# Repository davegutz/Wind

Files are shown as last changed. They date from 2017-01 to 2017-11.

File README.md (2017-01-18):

# Wind
Lab Project
  Verify controllability of turbine system designed elsewhere.
  
# Installation Instructions
1.  Install Link Shell Extension  http://download.cnet.com/Link-Shell-Extension-64-bit/3000-2248_4-75213087.html
        It will make you restart explorer.    
    Link Shell Manual:  http://www.howtogeek.com/howto/16226/complete-guide-to-symbolic-links-symlinks-on-windows-or-linux/
2.  Install Arduino:  Get Arduino .zip
        i.  https://www.arduino.cc/en/Main/Software    get the Windows ZIP file for non-admin install
        ii. Unzip into your “My Documents”
            Ref:  https://www.arduino.cc/en/Guide/PortableIDE  Summary follows so shouldn’t have to go here
		iii.When installed, it creates folder Arduino-1.x.x where you told it to.   This is the "root" in what follows.
3.  Browse to Arduino-1.x.x, the root, in the unzipped Arduino..   Create a new directory called “portable” alongside the others
4.  Launch the Arduino executable “arduino.exe” found in the root.  This is the IDE.
    a.  Create/Save shortcuts to taskbar and Start
    b.  IDE-File - preferences - uncheck "Show verbose output during compilation" - set Compiler warnings = none.
        Be sure to click OK even if made no changes (do not press “X”).
    c.  Close the IDE.   The defaults are now set.
5.  Browse to <root>/portable/sketchbook (Arduino-1.x.x) to create symbolic link to source
	a.  Browse to this installation folder, where this README.md file is kept.   This is <source> in what follows.
    b.  right-click on myWindCode in  <source>\portable\sketchbook and “pick link source”
    c.  right-click in <root>\portable\sketchbook.  Right-click - Drop-as - Symbolic link.
6.  Open the IDE.   File-open-browse to potWind.ino.   Click it open.
    Close all other IDE windows so IDE remembers your default choice.
     Reference: https://www.arduino.cc/en/Reference/HomePage
        In brief:  Ctrl-r to compile.   Try it now with potWind.    Ask for help if this does not work.
                   Ctrl-u to compile/upload.   Arduino needs to be connected and USB free
7.  Install CoolTerm USB monitor
    http://freeware.the-meiers.org/CoolTerm_Win.zip
    Copy CoolTerm_0.stc in this folder to the desktop for easy starting of USB
8.  Habitually calibrate your ESC:
        - Open loop on board
        - Set POT to max
        - Power the ESC.   Wait for musical phrase followed by two beeps in quick succession
        - Set POT to min.   Wait for three beeps followed by one ready beep.
    Calibration may last 100 runs or it may last 1 run.   Motion of the POT
    can undo calibration if you're not hearing all the beeps.  
    Beware of this.   It's the most common problem.
    When you start up get in the habit of spot-checking calibration:
        - Nt moves at throttle 5-15 deg
        - 80% Nt at throttle 180 deg
9.  Normal startup
    - Microcontroller powered and at 0 deg throttle (either open or closed loop); wind power supply off
    - Turn on wind power supply.    Wait and should hear 3 beeps followed by 1
10. Control checkout
    It is possible to close the loop using embedded model before firing up the turbine and damaging something.
    In potWind.ino set bareOrTest=True, recompile, reload, and run without turbine powered.
    Observe output as though running with turbine (feedback switched internally).
    The CLAW embedded model will have an erroneous Ng(throttle) characteristic because the Arduino throughput will not support a table lookup here.

# FAQ
1.  Coolterm “Port not found.”  
    Rescan ports in Coolterm-Connection-Options
    Restart Coolterm if necessary
    Turn off Arduino IDE USB monitor
2.  Suddenly bad stability.   Recalibrate ESC.
    When you start up get in the habit of spot-checking calibration:
        - Nt moves at throttle 5-15 deg
        - 80% Nt at throttle 180 deg
3.  No response.  Check for loose wires on board.
4.  Poor response.   Check for reversed wires on ESC to 3-phase. 
    Confirm direction of airflow into inlet of gas generator.
5.  Arduino IDE:  port not found following ctrl-u
    Arduino-Tools-Port-Select Arduino
6.  Simulink Wind_SIM:  Invalid setting in 'Wind_SIM/ESC_Core_Tur/Rate_Transition1' for parameter 'InitCond'
    There is a NaN in data vector.  It is probably the first row.
    Open MOD.source file and delete offending row.   Resave it and rerun Wind_SIM.
7.  Arduino IDE:  When compiling, "The system cannot find the path specified."   This means the IDE is opened in the wrong folder.    Start another IDE session by Arduino - File - Open or Open Recent. 

8.  Simulink Wind_SIM:  Multiple messages running Simulink Wind_SIM:   "x-values must be increasing."  or "Unsupported input format." There is data corruption in DS.V, easily fixed by hand.  Open the csv file.  Plot "time" all by itself with no x-values using excel plot.    See dropout.   Browse to row indicated by x-param.
9.  Simulink Wind_SIM:  Transient truncated Simulink Wind_SIM running with vectors.   There are data dropouts in csv file.  Browse in csv file to the truncated time and delete bad rows of data.
10. Simulink Wind_SIM:  There is an apparent mismatch between Nts and Nt_ref.  You are probably running in "test" mode.    Look at Figure 2 for these.
11. Arduino IDE:  When compiling, "The systsem cannot find the path specified."  The  means the IDE is opened in the wrong folder.   Start another IDE session by using IDE Arduino - File - Open - or Open Recent.
12. Simulink Wind_SIM:   "Reference to non-existent field 'tFinal'."  Cannot open the csv file.  Probably named badly.
13. Simulink Wind_SIM:  "Error du to multiple causes."  "Reference to non-existent field 'vpot'".  You have "CALIBRATING" set in myWindCode.ino.   You can re-run or rename vf2v to vpot in csv file and ignore it but this will cause initialization to go badly.   So write the real vpot into csv file as constant.
14.  Simulink Wind_SIM:  Why does Nts not equal NtsD?   Ng in the Simulink model is assumed to follow nominal trend, so same software logic can be used all units.   The real Ng is not nominal and will differ.

# Expected Results
Set "#define VECTOR" in potWind.ino
Recompile and upload
Select open or close loop mode as desired on board
Start CoolTerm data save
Press pushbutton on board to begin defined vector test
Stop CoolTerm data save when done
Compare to Saves/v<your kit #>_2017

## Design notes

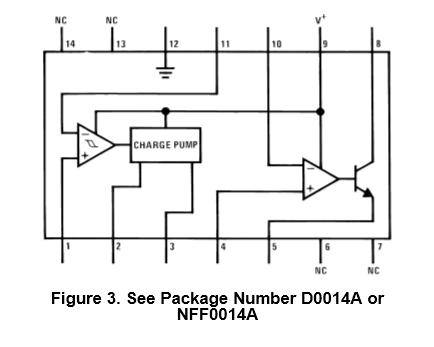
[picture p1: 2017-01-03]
Documentation/LM2907/LM2907 Schematic.PNG

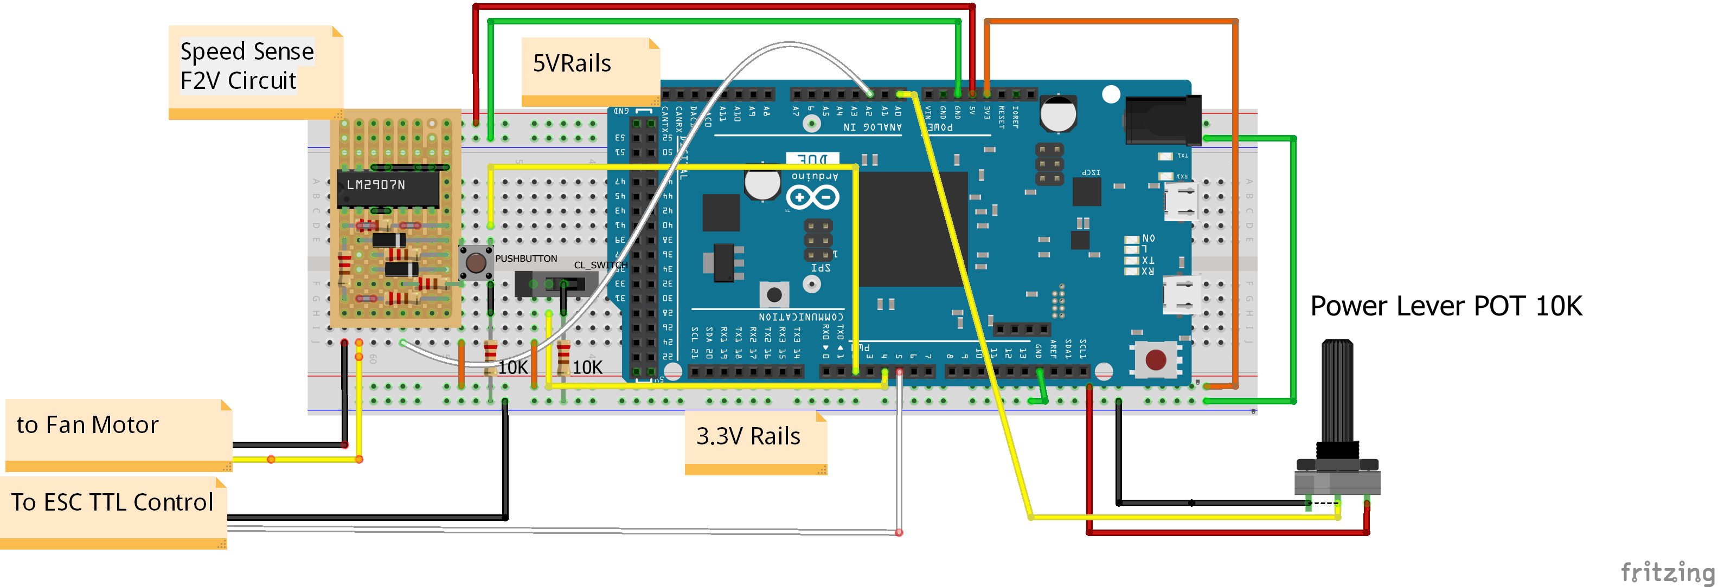
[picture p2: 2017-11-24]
Documentation/arduinoDUE_Wind_bb.png

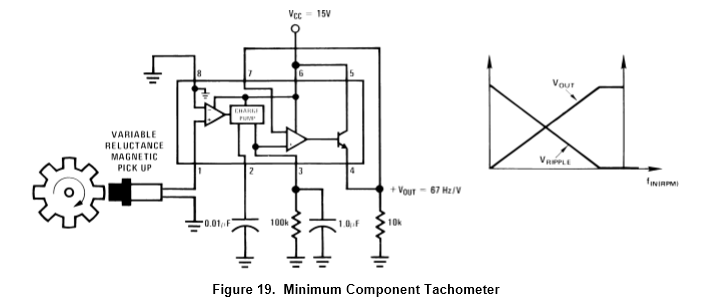
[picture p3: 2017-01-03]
Documentation/LM2907/LM2907 Circuit.PNG

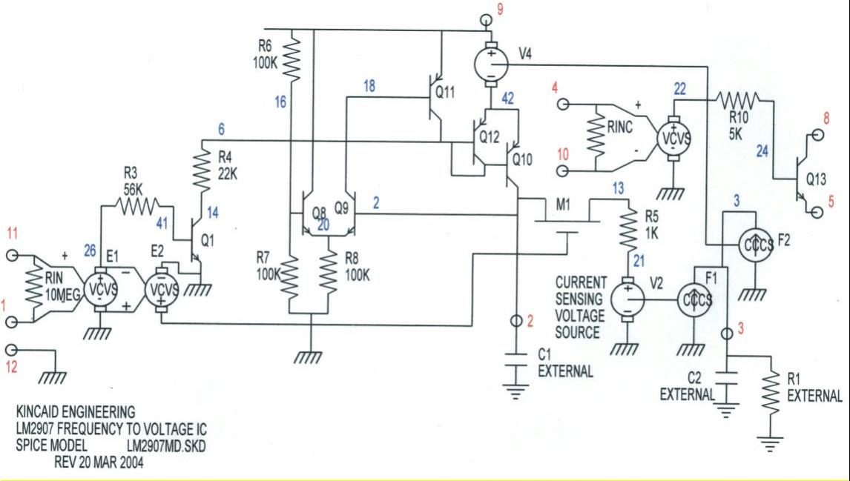
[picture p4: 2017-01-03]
Documentation/LM2907/LM2907.jpg

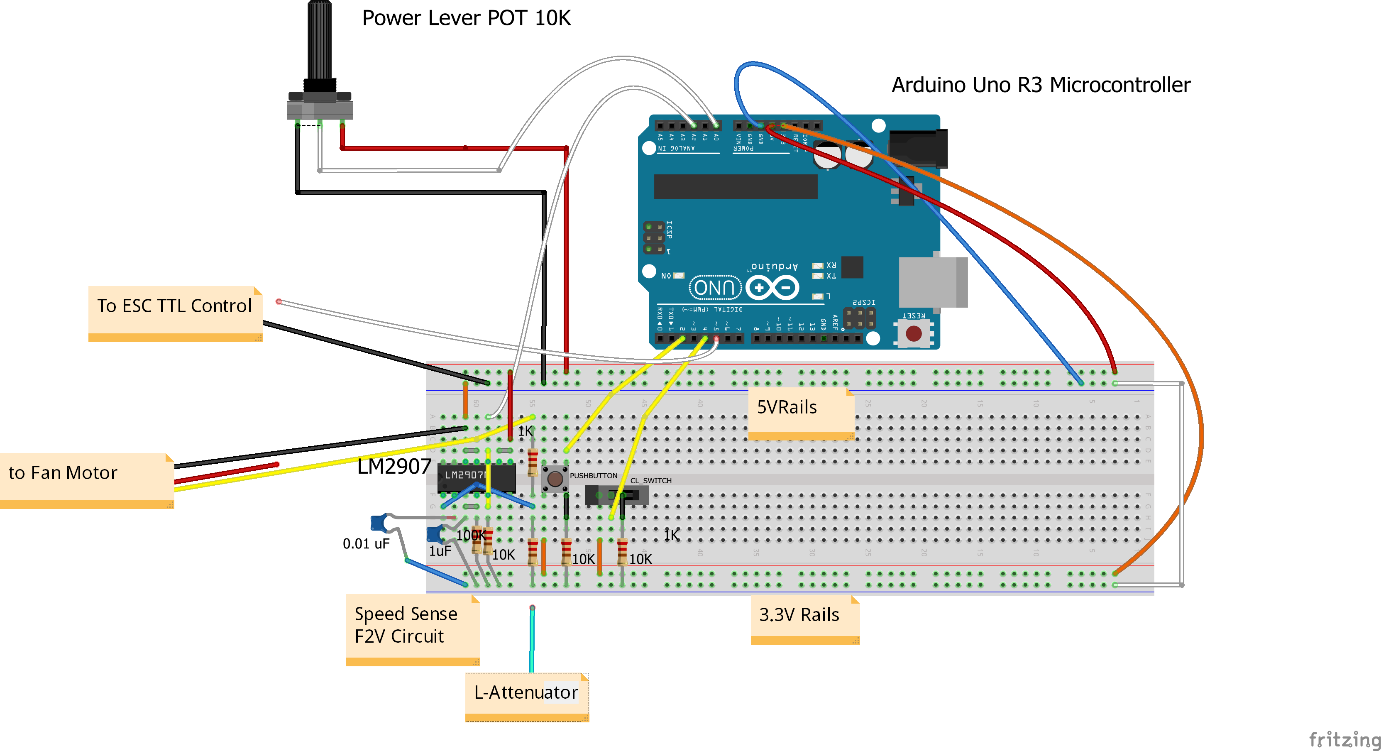
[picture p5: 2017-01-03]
Documentation/arduinoWind.png

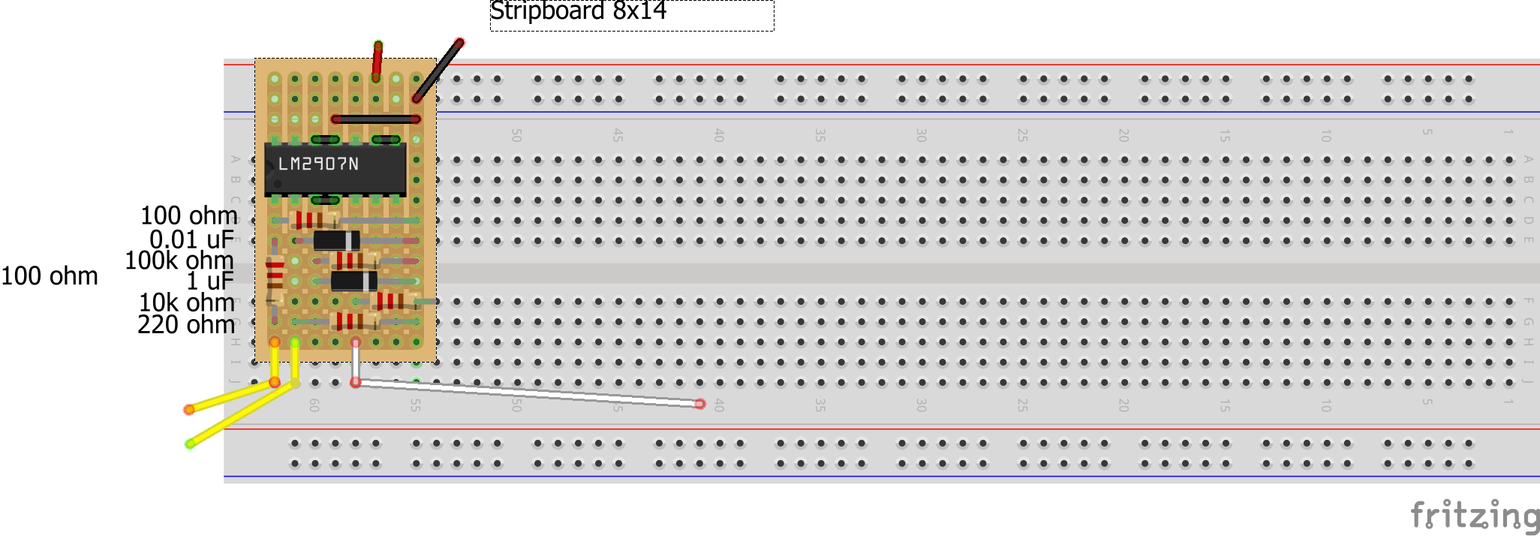
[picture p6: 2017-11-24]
Documentation/speedSenseStripboard_bb.png

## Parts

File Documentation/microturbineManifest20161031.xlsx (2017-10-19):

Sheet: 20161031
Manufacturer | Description | Part No | Source | Price Ea | Qty | Total | Shipping/Tax | $199.52
Hobby King | 50mm Alloy EDF 4800 kv (3s version) | Item# 20014254188 - 2x #107000044/22947 | https://hobbyking.com/en_us/hobbykingtm-50mm-alloy-edf-4800kv-3s-version.html | $20.26 | 2 | $40.52 | $8.43 | $48.95
Turnigy | Plush 25amp Speed Controller ESC | B00URCM4QO | http://www.hobbyking.com/hobbyking/store/__68532__TURNIGY_Plush_25amp_Speed_Controller_w_BEC_AR_Warehouse_.html | $18.89 | 1 | $18.89 | $6.96 | $25.85
Arduino | Uno R3 | A000066 | https://www.amazon.com/gp/product/B006H06TVG/ref=oh_aui_detailpage_o01_s00?ie=UTF8&psc=1 | $18.59 | 1 | $18.59 | $0.00 | $18.59
BINZET | Charger AC 100-240V to DC 12V 10A |  | https://www.amazon.com/gp/product/B00PK0N14M/ref=oh_aui_detailpage_o05_s00?ie=UTF8&th=1 | $17.99 | 1 | $17.99 | $0.00 | $17.99
Elegoo | Fun Kit | LYSB01ERPEMAC-ELECTRNCS | https://www.amazon.com/gp/product/B01ERPEMAC/ref=oh_aui_detailpage_o00_s00?ie=UTF8&psc=1 | $16.86 | 1 | $16.86 | $0.00 | $16.86
Fernco | PVC Couplings 2". Drill 7/32" hole for wires | P1056-22 | http://www.homedepot.com/p/2-in-x-2-in-DWV-Flexible-PVC-Coupling-P1056-22/100096490;jsessionid=FD5ADC11436A2B9FE7E68686A5A1567B | $4.99 | 2 | $9.98 | $0.56 | $10.54
Veranda | Cellular PVC Trim, 3/4 x 2-1/2 x 8' cut to 5" | H190JWS5 | http://www.homedepot.com/p/Veranda-3-4-in-x-2-1-2-in-x-8-ft-Cellular-PVC-Trim-H190JWS5/100243235 | $9.97 | 1 | $9.97 | $0.56 | $10.53
Home Depot | Toolbox | 17331512 | http://www.homedepot.com/p/The-Home-Depot-19-in-Plastic-Tool-Box-with-Metal-Latches-and-Removable-Tool-Tray-17331512/202021300 | $8.97 | 1 | $8.97 | $0.50 | $9.47
Mouser | Mouser Shipping | --- | http://www.mouser.com | $0.00 | 1 | $0.00 | $8.00 | $8.00
BW | 20 pairs 2mm Gold Plated Bueelt Banana Plug Connectors for ESC Batter |  | https://www.amazon.com/gp/product/B00T5SW7FE/ref=oh_aui_detailpage_o08_s00?ie=UTF8&psc=1 | $6.89 | 1 | $6.89 | $0.00 | $6.89
Generic | PVC Pipe 2" Sch 40, cut to 5" | 531137 | http://www.homedepot.com/p/2-in-x-10-ft-280-PSI-Schedule-40-PVC-DWV-Plain-End-Pipe/100161954 | $6.38 | 1 | $6.38 | $0.36 | $6.74
Commercial Electric | 3-way extension plug for 115 AC | # LA-05 | http://www.homedepot.com/p/Commercial-Electric-15-Amp-Triplex-Outlet-Swivel-Tap-White-LA-05/204836952 | $4.58 | 1 | $4.58 | $0.26 | $4.84
Generic | Pencil box > 6-3/4x4-1/2x1-1/2 inside |  | https://www.amazon.com/ADVANTUS-Polypropylene-Pencil-Inches-34104/dp/B0014DZE8K?s=office-products | $3.95 | 1 | $3.95 | $0.22 | $4.17
Gardner Bender | Shrink Tubing, 5 pk 3/16" black | HST-187B | http://www.homedepot.com/p/Gardner-Bender-3-16-in-Black-Polyolefin-Heat-Shrink-Tubing-5-Pack-HST-187B/202797315 | $1.99 | 1 | $1.99 | $0.11 | $2.10
Texas Instruments | Demodulator 10 kHz, through hole | LM2907N/NOPB | http://www.mouser.com/Search/ProductDetail.aspx | $1.91 | 1 | $1.91 | $0.00 | $1.91
Alpha | Potentiometer Linear, 10K, 20%, 500V | RV24AF-22-15R1-B10K-3LA | http://www.mouser.com/Search/ProductDetail.aspx | $1.61 | 1 | $1.61 | $0.00 | $1.61
Kemet | Cap .01 uF 5% 50 VDC | SMR5103J50J01L16.5CBULK | http://www.mouser.com/Search/ProductDetail.aspx | $0.63 | 1 | $0.63 | $0.04 | $0.67
Vimex | Slide Switch SPDT, 30V 200mA | 612-EG1218 | http://www.mouser.com/ProductDetail/E-Switch/EG1218/?qs=sGAEpiMZZMtHXLepoqNyVZDOWY7elTCOE4MJ3sXRkSs%3d | $0.56 | 1 | $0.56 | $2.13 | $2.69
Kemet | Cap 1 uF, 20 VDC, 5% | T356A105J020AT | http://www.mouser.com/ProductDetail/Kemet/T356A105J020AT/?qs=sGAEpiMZZMtZ1n0r9vR22XCieDCNbX8FzsYaQmMDgkk%3d | $0.85 | 1 | $0.85 | $0.05 | $0.90
Kemet | Cap 10 uF, 25 VDC, 20% | EEA-GA1E100 | http://www.mouser.com/ProductDetail/Panasonic/EEA-GA1E100/ | $0.22 | 1 | $0.22 | $0.01 | $0.23
Lenovo | Thinkpad X1 Laptop, GE Provided | n/a | n/a | - | 1 | - | - | -
Arduino | Portable IDE | n/a | https://www.arduino.cc/en/Guide/PortableIDE | - | 1 | - | - | -

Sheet: 20171019
Manufacturer | Description | Part No | Source | Price Ea | Qty | Total | Shipping/Tax | $347.36
BINZET | Spare power supplies | Charger AC 100-240V to DC 12V 10A | https://www.amazon.com/gp/product/B00PK0N14M/ref=oh_aui_search_detailpage?ie=UTF8&psc=1 | $17.99 | 2 | $35.98 | $0.00 | $35.98
Arduino | PLC for Simulink | DUE | https://www.amazon.com/Arduino-org-A000062-Arduino-Due/dp/B00A6C3JN2?s=electronics | $44.47 | 5 | $222.35 | $0.00 | $222.35
Toshiba | MOSFET for auto calibrate | TK40A06N1 | http://www.mouser.com/Search/ProductDetail.aspx | $0.98 | 6 | $5.88 | $0.00 | $5.88
Meder | Relays for auto calibrate | SIL03-1A72-71D | http://www.mouser.com/ProductDetail/MEDER-electronic-Standex/SIL03-1A72-71D/ | $3.98 | 6 | $23.88 | $0.00 | $23.88
Bourns | Carbon Potentiometers for Noise | PTD901-1015K-B103 | http://www.mouser.com/ProductDetail/Bourns/PTD901-1015K-B103/?qs=sGAEpiMZZMtC25l1F4XBU4LIzrlRxKBZVvfXJLawdTQ%3d | $1.68 | 5 | $8.40 | $0.00 | $8.40
Home Depot | PVC for base mounts, 3/4 x 7-1/4 x 96 | H190RWS4 | http://www.homedepot.com/p/Veranda-HP-3-4-in-x-7-1-4-in-x-8-ft-High-Performance-Cellular-PVC-Trim-H190RWS4/100290245 | $27.97 | 1 | $27.97 | $0.00 | $27.97
Hobby King | Spare turbine blades |  | https://hobbyking.com/en_us/rotor-for-hobbyking-alloy-50mm-edf-unit.html | $1.98 | 5 | $9.90 | $5.00 | $14.90
Mouser | Mouser Shipping | --- | http://www.mouser.com | $0.00 | 1 | $0.00 | $8.00 | $8.00
 |  |  |  |  |  | $0.00 | $0.00 | $0.00

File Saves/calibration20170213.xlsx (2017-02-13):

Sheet: Ard0_Turn0_ESC0_G0b_T0a
Description | Set Nt | TTL, ms | throttleFlt, deg | v4, vdc | Charger V, vdc | Charger I, A | Tng, micros | Ttur, micros |  | Charger Pwr, W | Throttle, deg | ln(Throttle) | FreqNg, Hz | FreqTur, Hz | Ng, RPM | Nt, RPM | Ng, % | Nt, % | Throttle, deg | Charger Pwr, W | Ng Pwr, W | Ng Pwr, SHP | Ng Total Torque, ft-lbf | Ng Torque, ft-lbf | Thrust, N | Thrust Power, W | Overall Efficiency | Vw, m/s | Vw, mph | Vt, m/s | Lambda tip speed ratio | dCpdLambda | simulate vpot from throttle | model throttle from vpot | Model Ng from Model Throttle, rpm | Model Ng from Model Throttle, % | Model pcntRef from Model Ng, % | Model Ng from pcntRef at RESET, % | Model Nt from Model Ng, % | Model Nt from Model Ng, rpm | Model Qg from Model Ng, ft-lbf | Model PwrG from Model Ng*Q, shp | Model dQgdNg, ft-lbf/rpm | Model TauG | Model dQtdNt, ft-lbf/rpm | Model TauT from wind | v4, vdc
DC Power Overhead | n/a | 1.03 | 6.07 | 0.0032 | 12.24 | 0.019 | 1e+32 | 1e+32 |  | 0.2 | 6.07 | 1.8027 | 1e-26 | 1e-26 | 6e-25 | 0 | 1.302083333e-27 | 0 | 6.066122035 | 0.23 | 0 | 0.0000 | 0.00000 | 0.00000 | 9.768434808e-87 | 9.469612349e-129 |  | 1.938818764e-42 | 4.362342218e-42 | 0 | 0.00 |  | 0.169 | 6.066 | 0.00 | 0.00 | -17.48 | 0.03 |  | 0 |  |  |  |  |  |  | 0.0032
Lowest Ng | n/a | 1.05 | 9 | 0.0024 | 12.15 | 0.34 | 7080 | 1e+32 |  | 4.1 | 9 | 2.1972 | 141.2429379 | 1e-26 | 8474.576271 | 6e-25 | 18.39100753 | 1.302083333e-27 | 9 | 4.07 | 3.83769 | 0.0051 | 0.00319 | 0.00000 | 0.028 | 0.04 | 1.1 | 3.25 | 7.3 | 1.727875959e-27 | 5.309152921e-28 |  | 0.250 | 9.000 | 4918.12 | 10.67 | -7.36 | 10.70 |  | 0 | 0.00000 | 0.00000 | 1.105647023e-07 |  |  |  | 0.0024
First Nt | tbd | 1.11 | 20 | 0.069 | 12.14 | 0.86 | 4040 | 68000 |  | 10.5 | 20 | 2.9957 | 247.5247525 | 14.70588235 | 14851.48515 | 882.3529412 | 32.22978548 | 1.914828431 | 20 | 10.45 | 10.22 | 0.0137 | 0.00485 | 0.00166 | 0.148 | 0.56 | 5.4 | 7.55 | 17.0 | 2.5 | 0.34 |  | 0.556 | 20.000 | 14872.75 | 32.28 | 13.10 | 32.29 | 13.1 | 6038.54 | 0.00194 | 0.00548 | 3.729326807e-07 | 0.100 |  |  | 0.069
Dynamic Nt #1 | 16 | 1.14 | 25 | 0.51 | 12.14 | 1.13 | 3680 | 8500 |  | 13.7 | 25 | 3.2189 | 271.7391304 | 117.6470588 | 16304.34783 | 7058.823529 | 35.38269928 | 15.31862745 | 25 | 13.72 | 13.49 | 0.0181 | 0.00583 | 0.00264 | 0.196 | 0.85 | 6.2 | 8.68 | 19.5 | 20.3 | 2.34 |  | 0.694 | 25.000 | 17654.58 | 38.31 | 18.82 | 38.33 | 18.8 | 8674.185965 | 0.00308 | 0.01034 | 4.462516013e-07 | 0.084 | -1.105608516e-07 | 0.339 | 0.51
Dynamic Nt #2 | 20 | 1.19 | 35 | 0.801 | 12.11 | 1.838 | 2980 | 5420 |  | 22.3 | 35 | 3.5553 | 335.5704698 | 184.501845 | 20134.22819 | 11070.1107 | 43.69407159 | 24.02367774 | 35 | 22.26 | 22.03 | 0.0295 | 0.00770 | 0.00452 | 0.369 | 2.20 | 9.9 | 11.92 | 26.8 | 31.9 | 2.67 |  | 0.972 | 35.000 | 21849.23 | 47.42 | 27.45 | 47.43 | 27.4 | 12648.40654 | 0.00518 | 0.02155 | 5.568072553e-07 | 0.067 | -1.517220518e-07 | 0.247 | 0.801
Dynamic Nt #3 | 25 | 1.30 | 54 | 1.167 | 12.06 | 3.18 | 2390 | 3740 |  | 38.4 | 54 | 3.9890 | 418.4100418 | 267.3796791 | 25104.60251 | 16042.78075 | 54.4804742 | 34.81506239 | 54 | 38.35 | 38.12 | 0.0511 | 0.01069 | 0.00750 | 0.716 | 5.94 | 15.5 | 16.59 | 37.3 | 46.2 | 2.78 |  | 1.500 | 54.000 | 27255.18 | 59.15 | 38.56 | 59.15 | 38.6 | 17770.27059 | 0.00857 | 0.04450 | 6.992882824e-07 | 0.054 | -2.112400453e-07 | 0.177 | 1.167
Dynamic Nt #4 | 36 | 1.36 | 64 | 1.275 | 12.03 | 3.96 | 2170 | 3260 |  | 47.6 | 64 | 4.1589 | 460.8294931 | 306.7484663 | 27649.76959 | 18404.90798 | 60.00384025 | 39.94120654 | 64 | 47.64 | 47.41 | 0.0636 | 0.01208 | 0.00889 | 0.956 | 9.17 | 19.2 | 19.18 | 43.2 | 53.0 | 2.76 |  | 1.778 | 64.000 | 29373.23 | 63.74 | 42.92 | 63.75 | 42.9 | 19777.02234 | 0.01011 | 0.05657 | 7.551124993e-07 | 0.050 | -2.441650521e-07 | 0.153 | 1.275
Dynamic Nt #5 | 45 | 1.50 | 90 | 1.597 | 11.95 | 5.94 | 1860 | 2690 |  | 71.0 | 90 | 4.4998 | 537.6344086 | 371.7472119 | 32258.06452 | 22304.83271 | 70.00448029 | 48.40458488 | 90 | 70.98 | 70.75 | 0.0949 | 0.01545 | 0.01226 | 1.518 | 18.35 | 25.8 | 24.17 | 54.4 | 64.2 | 2.658 |  | 2.500 | 90.000 | 33623.41 | 72.97 | 51.66 | 72.97 | 51.7 | 23803.85519 | 0.01356 | 0.08682 | 8.67131732e-07 | 0.043 | -3.076831315e-07 | 0.122 | 1.597
Dynamic Nt #6 | 50 | 1.69 | 125 | 1.95 | 11.84 | 8.59 | 1620 | 2210 |  | 101.7 | 125 | 4.8283 | 617.2839506 | 452.4886878 | 37037.03704 | 27149.32127 | 80.3755144 | 58.91779789 | 125 | 101.71 | 101.47 | 0.1361 | 0.01930 | 0.01611 | 2.298 | 34.16 | 33.6 | 29.73 | 66.9 | 78.2 | 2.629 |  | 3.472 | 125.000 | 37718.72 | 81.85 | 60.08 | 81.85 | 60.1 | 27683.96023 | 0.01733 | 0.12449 | 9.750692614e-07 | 0.038 | -3.785302413e-07 | 0.099 | 1.95
Dynamic Nt #7 | 52 | 1.86 | 155 | 2.26 | 11.66 | 12.52 | 1430 | 1900 |  | 146.0 | 155 | 5.0434 | 699.3006993 | 526.3157895 | 41958.04196 | 31578.94737 | 91.05477855 | 68.53070175 | 155 | 145.98 | 145.75 | 0.1955 | 0.02447 | 0.02128 | 3.341 | 59.89 | 41.0 | 35.85 | 80.7 | 90.9 | 2.536 | -0.425 | 4.306 | 155.000 | 40400.42 | 87.67 | 65.59 | 87.67 | 65.6 | 30224.73471 | 0.02004 | 0.15419 | 1.045749028e-06 | 0.036 | -4.564246037e-07 | 0.082 | 2.26
Dynamic Nt #7 | 52 | 1.92 | 165 | 2.34 | 11.56 | 14.28 | 1380 | 1815 |  | 165.1 | 165 | 5.1059 | 724.6376812 | 550.9641873 | 43478.26087 | 33057.85124 | 94.35386473 | 71.74012856 | 165 | 165.08 | 164.84 | 0.2211 | 0.02670 | 0.02351 | 3.717 | 70.29 | 42.6 | 37.82 | 85.1 | 95.2 | 2.517 | -0.400 | 4.583 | 165.000 | 41179.84 | 89.37 | 67.19 | 89.36 | 67.2 | 30963.18996 | 0.02087 | 0.16361 | 1.066291522e-06 | 0.035 | -4.814536392e-07 | 0.078 | 2.34
Max | tbd | 2.00 | 180 | 2.4 | 11.53 | 14.92 | 1368 | 1790 |  | 172.0 | 180 | 5.1930 | 730.994152 | 558.6592179 | 43859.64912 | 33519.55307 | 95.18153021 | 72.74208566 | 180 | 172.03 | 171.80 | 0.2304 | 0.02759 | 0.02440 | 4.425 | 91.30 | 53.1 | 41.26 | 92.8 | 96.5 | 2.339 |  | 5.000 | 180.000 | 42264.57 | 91.72 | 69.42 | 91.71 | 69.4 | 31990.91934 | 0.02204 | 0.17736 | 1.094881102e-06 | 0.034 | -5.253091111e-07 | 0.071 | 2.4
Calibration sheet
1 |  | Calibrate the ESC first |  |  |  |  |  | Key | User Inputs
2 |  | Update the Arduino software |  |  |  |  |  |  | Derived
3 |  | Run the points below |  |  |  |  |  |  | Entry to myCLAW.h and potESC.ino
4 |  | Enter blue highlighted items into myCLaw.h |  |  |  |  |  |  | Entry to myCLAW.h and potESC.ino; same between units
5 |  | Run the frequency response fr_
6 |  | Enter results of fr_ into table lower right corner this sheet
7 |  | Hand tune DELTAV |  |  |  |  |  |  |  |  |  |  |  |  | // Constants always defined - potESC.ino #ifdef Arduino
8 |  | Check that Nt corresponding to entry in column AG lines up with Nt from Z in Tau data |  |  |  |  |  |  |  |  |  |  |  |  | POT_MAX | 5 |  |  | v
 |  |  |  |  |  |  |  |  |  |  |  |  |  |  | F2V_MAX | 5 |  |  | v
Motor | numPoles | 1 |  |  |  |  |  | Inertia Turbine Only (need motor***) |  |  |  |  |  |  | F2V_MIN | 0 |  |  | v
 | Kv | 4800 | rpm/V |  |  |  |  | Rt= | 25 | mm |  |  |  |  | POT_MIN | 0 |  |  | v
 | Vc | 12 |  |  |  |  |  | Mt= | 2.1797 | gm |  |  |  |  | DENS_SI | 1.225 |  |  | kg/m^3
 | Ra | 0.0399 | O |  |  |  |  | Jt= | 0.001548498305 | lbm-in^2 | 1/3*MR^2
 | La | 4.2e-06 | H |  |  |  |  | Rm= | 4.8 | mm | at most |  |  |  | // See calibration<date>.xlsx - myCLAW.h
 | Power | 240 | W max |  |  |  |  | Lm= | 19.0 | mm | at most |  |  |  | RPM_P | 460.8 |  |  | rpm/%
 | Kvrps | 502.7 | r/s / V |  |  |  |  | Mm= | 0.006212622191 | lbm | at most |  |  |  | THTL_MAX | 180 |  |  | deg
 | Kt | 0.0139 | ft-lbf/A |  |  |  |  | Jm | 0.0001092062495 | lbm-in^2 | 1/2*MR^2 |  |  |  | THTL_MIN | 0 |  |  | deg
 | Fn | 0.99 | lbf |  |  |  |  | J= | 0.001657704555 | lbm-in^2 |  |  |  |  | AREA_SI | 0.002121360439 |  |  | m^2
 |  |  |  |  |  |  |  | J= | 1.151183719e-05 | lbm-ft^2 |  |  |  |  | NM_2_FTLBF | 0.738 |  |  | ft-lbf/N-m
LM2907N Circuit |  | vf2v, v |  |  |  |  |  | J= | 3.74268175e-08 | ft-lbf/(rpm/sec) |  |  |  |  | JT | 3.74268175e-08 |  |  | rpm/s / ft-lbf
 | F2V_MIN | 0 |  |  |  |  |  |  |  |  |  |  |  |  | D_SI | 0.055 |  |  | m
 | F2V_MAX | 5 |  |  |  | TBD |  | From fr_a0_t0_e0_g0b_t0a.xlsx |  |  |  |  |  |  | FG_SI | 4.425 |  |  | N
 |  |  |  |  |  |  |  | Nt, % | Calc Ng, % | Meas TauT0, s | Meas QdN, ft-lbf/rpm | Meas dQdN, N-m/rpm
Fan Rotor | Dia | 55 | mm |  |  |  |  | 83.9 | 107.0 | 0 |  |  |  |  | // Ard0_Turn0_ESC0_G0b_T0a - myCLAW.h
 | Dia spinner | 18 | mm |  |  |  |  | 62 | 83.9 | 0.050 |  |  |  |  | P_V4_NT | 0 | 13952.04806 | 27.10040275 | rpm
 |  |  |  |  |  |  |  | 48 | 69.1 | 0.082 | 4.564246037e-07 | -6.187291928e-07 | cal point |  | P_LT_NG | -22473.69517 | 12466.55113 |  | rpm
Air | Dens | 1.225 | kg/m^3 | SLS Std Day |  |  |  | 25 | 44.8 | 0.196 |  |  |  |  | P_NG_NT | -8052.654718 | 0.9475 |  | rpm
 |  |  |  |  |  |  |  | 16 | 35.3 | 0.249 |  |  |  |  | P_NT_NG | 8510.224957 | 1.0550 |  | rpm
Thtl | min | 0 | V Pot |  |  |  |  | -26.6 | -9.6 | 0.5 |  |  |  |  | DCPDL | -0.425 |  |  | none
 | max | 5 | V Pot |  |  |  |  |  |  |  |  |  |  |  | LAMBDA | 2.54 |  |  | none
 | min | 0 | deg Throttle |  |  |  |  |  |  |  |  |  |  |  | DELTAV | 0 |  |  | m/s
 | max | 180 | deg Throttle |  |  |  |  | P_NG_QG | -0.000695441078 | -1.905896073e-08 | 1.317817906e-11 | ft-lbf
Adjust | 1.25 | for 100% Ng at |  | 240 | watts |  |  | matlabTuning.xlsx |  |  |  | tldF=.15, tlgF=.03
 |  |  |  |  |  |  |  | TauT Design, s | Nt, % | TLD_S | LG_S | TLD_L | LG_L |  | xAll | 0.0 | -0.1 | 27.2 | 47.4 | 75.1 | 80.0
 |  |  |  |  |  |  |  | 0 | 83.9 | 0.2 | 4.4 | 0.09 | 5 |  | TLD_S | 0.475 | 0.475 | 0.325 | 0.225 | 0.200 | 0.200 | Scheduled
 |  |  |  |  |  |  |  | 0.02 | 75.1 | 0.2 | 3.75 | 0.09 | 5 |  | LG_S | 2.40 | 2.40 | 2.70 | 3.20 | 3.75 | 4.40
 |  |  |  |  |  |  |  | 0.085 | 47.4 | 0.225 | 3.2 | 0.125 | 4.050 |  | tldF | 0.15
 |  |  |  |  |  |  |  | 0.185 | 27.2 | 0.325 | 2.7 | 0.24 | 3.75 |  | tlgF | 0.03
 |  |  |  |  |  |  |  | 0.344 | -0.1 | 0.475 | 2.4 | 0.42 | 3.6 |  | TLD_L | 0.420 | 0.420 | 0.240 | 0.125 | 0.090 | 0.090 | Fixed lead
 |  |  |  |  |  |  |  | 0.5 | -26.6 | 0.475 | 2.4 | 0.42 | 3.6 |  | LG_L | 3.60 | 3.60 | 3.75 | 4.05 | 5.00 | 5.00

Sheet: Ard1_Turn1x_ESC1_G1b_T1a
Description | Set Nt | TTL, ms | throttleFlt, deg | v4, vdc | Charger V, vdc | Charger I, A | Tng, micros | Ttur, micros |  | Charger Pwr, W | Throttle, deg | ln(Throttle) | FreqNg, Hz | FreqTur, Hz | Ng, RPM | Nt, RPM | Ng, % | Nt, % | Throttle, deg | Charger Pwr, W | Ng Pwr, W | Ng Pwr, SHP | Ng Total Torque, ft-lbf | Ng Torque, ft-lbf | Thrust, N | Thrust Power, W | Overall Efficiency | Vw, m/s | Vw, mph | Vt, m/s | Lambda tip speed ratio | dCpdLambda | simulate vpot from throttle | model throttle from vpot | Model Ng from Model Throttle, rpm | Model Ng from Model Throttle, % | Model pcntRef from Model Ng, % | Model Ng from pcntRef at RESET, % | Model Nt from Model Ng, % | Model Nt from Model Ng, rpm | Model Qg from Model Ng, ft-lbf | Model PwrG from Model Ng*Q, shp | Model dQgdNg, ft-lbf/rpm | Model TauG | Model dQtdNt, ft-lbf/rpm | Model TauT from wind | v4, vdc
DC Power Overhead | n/a | 1.03 | 5.38 | 0.0032 | 12.24 | 0.019 | 1e+32 | 1e+32 |  | 0.2 | 5.38 | 1.6827 | 1e-26 | 1e-26 | 6e-25 | 0 | 1.302083333e-27 | 0 | 5.380330042 | 0.23 | 0 | 0.0000 | 0.00000 | 0.00000 | 9.768434808e-87 | 9.469612349e-129 |  | 1.938818764e-42 | 4.362342218e-42 | 0 | 0.00 |  | 0.149 | 5.380 | 0.00 | 0.00 | -12.59 | 0.04 |  | 0 |  |  |  |  |  |  | 0.0032
Lowest Ng | n/a | 1.04 | 8 | 0.0046 | 12.23 | 0.28 | 8000 | 1e+32 |  | 3.4 | 8 | 2.0794 | 125 | 1e-26 | 7500 | 6e-25 | 16.27604167 | 1.302083333e-27 | 8 | 3.39 | 3.15515 | 0.0042 | 0.00296 | 0.00000 | 0.019 | 0.03 | 0.8 | 2.71 | 6.1 | 1.727875959e-27 | 6.376910601e-28 |  | 0.222 | 8.000 | 4555.17 | 9.89 | -2.93 | 9.92 |  | 0 | 0.00000 | 0.00000 | 2.827231837e-07 |  |  |  | 0.0046 |  | -12.400000
First Nt | tbd | 1.07 | 12 | 0.238 | 12.25 | 0.53 | 5540 | 13200 |  | 6.5 | 12 | 2.4849 | 180.5054152 | 75.75757576 | 10830.32491 | 4545.454545 | 23.50330927 | 9.864267677 | 12 | 6.47 | 6.24 | 0.0084 | 0.00405 | 0.00109 | 0.057 | 0.14 | 2.1 | 4.70 | 10.6 | 13.1 | 2.78 |  | 0.333 | 12.000 | 9211.08 | 19.99 | 6.94 | 20.01 | 6.9 | 3198.660363 | 0.00033 | 0.00058 | 3.695740461e-07 | 0.101 |  |  | 0.238 |  | 72.50000
Dynamic Nt #1 | 16 | 1.09 | 17 | 0.434 | 12.24 | 0.655 | 4900 | 10000 |  | 8.0 | 17 | 2.8332 | 204.0816327 | 100 | 12244.89796 | 6000 | 26.57312925 | 13.02083333 | 17 | 8.02 | 7.78 | 0.0104 | 0.00448 | 0.00151 | 0.083 | 0.23 | 2.9 | 5.65 | 12.7 | 17.3 | 3.06 |  | 0.472 | 17.000 | 13210.65 | 28.67 | 15.42 | 28.69 | 15.4 | 7105.794506 | 0.00196 | 0.00492 | 4.44181543e-07 | 0.084 |  |  | 0.434
Dynamic Nt #2 | 20 | 1.12 | 21 | 0.586 | 12.24 | 0.877 | 4180 | 7500 |  | 10.7 | 21 | 3.0445 | 239.2344498 | 133.3333333 | 14354.06699 | 8000 | 31.15031898 | 17.36111111 | 21 | 10.73 | 10.50 | 0.0141 | 0.00515 | 0.00219 | 0.134 | 0.48 | 4.5 | 7.17 | 16.1 | 23.0 | 3.21 |  | 0.583 | 21.000 | 15637.09 | 33.93 | 20.56 | 33.95 | 20.6 | 9476.15657 | 0.00309 | 0.00920 | 4.89444074e-07 | 0.076 | -1.031450924e-07 | 0.363 | 0.586 | 0.44 | -8.506094887e-08
Dynamic Nt #3 | 25 | 1.15 | 27 | 0.793 | 12.23 | 1.23 | 3540 | 5580 |  | 15.0 | 27 | 3.2958 | 282.4858757 | 179.2114695 | 16949.15254 | 10752.68817 | 36.78201507 | 23.33482676 | 27 | 15.04 | 14.81 | 0.0199 | 0.00615 | 0.00319 | 0.220 | 1.01 | 6.7 | 9.21 | 20.7 | 31.0 | 3.36 |  | 0.750 | 27.000 | 18522.91 | 40.20 | 26.68 | 40.21 | 26.7 | 12295.27891 | 0.00458 | 0.01615 | 5.43275771e-07 | 0.069 | -1.436319949e-07 | 0.261 | 0.793
Dynamic Nt #4 | 36 | 1.23 | 42 | 1.175 | 12.19 | 2.41 | 2770 | 3760 |  | 29.4 | 42 | 3.7377 | 361.0108303 | 265.9574468 | 21660.64982 | 15957.44681 | 47.00661853 | 34.62987589 | 42 | 29.38 | 29.15 | 0.0391 | 0.00948 | 0.00651 | 0.460 | 3.06 | 10.4 | 13.30 | 29.9 | 46.0 | 3.46 |  | 1.167 | 42.000 | 23596.43 | 51.21 | 37.44 | 51.21 | 37.4 | 17251.54263 | 0.00758 | 0.03404 | 6.37916604e-07 | 0.059 | -2.252395456e-07 | 0.166 | 1.175 | 0.289 | -1.295045588e-07
Dynamic Nt #5 | 45 | 1.37 | 67 | 1.624 | 12.13 | 4.27 | 2170 | 2810 |  | 51.8 | 67 | 4.2047 | 460.8294931 | 355.8718861 | 27649.76959 | 21352.31317 | 60.00384025 | 46.33748517 | 67 | 51.80 | 51.56 | 0.0691 | 0.01313 | 0.01017 | 0.956 | 9.17 | 17.7 | 19.18 | 43.2 | 61.5 | 3.206 |  | 1.861 | 67.000 | 28959.21 | 62.85 | 48.81 | 62.84 | 48.8 | 22490.37824 | 0.01127 | 0.06212 | 7.379532029e-07 | 0.051 | -3.424745996e-07 | 0.109 | 1.624
Dynamic Nt #7 | 52 | 1.44 | 79 | 1.786 | 12.09 | 5.32 | 2020 | 2560 |  | 64.3 | 79 | 4.3694 | 495.049505 | 390.625 | 29702.9703 | 23437.5 | 64.45957096 | 50.86263021 | 79 | 64.32 | 64.09 | 0.0859 | 0.01520 | 0.01223 | 1.185 | 12.65 | 19.7 | 21.36 | 48.0 | 67.5 | 3.161 | -0.830 | 2.194 | 79.000 | 30851.07 | 66.95 | 52.82 | 66.94 | 52.8 | 24338.52187 | 0.01270 | 0.07457 | 7.732438699e-07 | 0.048 | -3.858434794e-07 | 0.097 | 1.786
Dynamic Nt #8 | 55 | 1.47 | 84 | 1.842 | 12.08 | 5.63 | 1970 | 2480 |  | 68.0 | 84 | 4.4308 | 507.6142132 | 403.2258065 | 30456.85279 | 24193.54839 | 66.09560068 | 52.50336022 | 84 | 68.01 | 67.78 | 0.0909 | 0.01567 | 0.01271 | 1.278 | 14.17 | 20.8 | 22.17 | 49.9 | 69.7 | 3.142 |  | 2.333 | 84.000 | 31555.77 | 68.48 | 54.31 | 68.47 | 54.3 | 25026.92869 | 0.01324 | 0.07958 | 7.863891339e-07 | 0.048 | -4.021532182e-07 | 0.093 | 1.842 | 0.085 | -4.403155001e-07
Dynamic Nt #8 | 62 | 1.67 | 121 | 2.19 | 11.97 | 8.66 | 1650 | 2040 |  | 103.7 | 121 | 4.7958 | 606.0606061 | 490.1960784 | 36363.63636 | 29411.76471 | 78.91414141 | 63.82761438 | 121 | 103.66 | 103.43 | 0.1387 | 0.02003 | 0.01707 | 2.175 | 31.45 | 30.3 | 28.93 | 65.1 | 84.7 | 2.928 |  | 3.361 | 121.000 | 35746.72 | 77.58 | 63.20 | 77.56 | 63.2 | 29121.02568 | 0.01670 | 0.11369 | 8.645667232e-07 | 0.043 | -5.367879663e-07 | 0.070 | 2.19
Max | tbd | 1.97 | 175 | 2.66 | 11.7 | 14.72 | 1360 | 1620 |  | 172.2 | 175 | 5.1648 | 735.2941176 | 617.2839506 | 44117.64706 | 37037.03704 | 95.74142157 | 80.3755144 | 175 | 172.22 | 171.99 | 0.2306 | 0.02746 | 0.02449 | 4.425 | 91.30 | 53.0 | 41.26 | 92.8 | 106.7 | 2.585 |  | 4.861 | 175.000 | 39983.86 | 86.77 | 72.18 | 86.75 | 72.2 | 33260.23592 | 0.02054 | 0.15633 | 9.436057589e-07 | 0.040 | -7.827245676e-07 | 0.048 | 2.66 | 0.035 | -1.069337643e-06
Calibration sheet
1 |  | Calibrate the ESC first |  |  |  |  |  | Key | User Inputs
2 |  | Update the Arduino software |  |  |  |  |  |  | Derived
3 |  | Run the points below |  |  |  |  |  |  | Entry to myCLAW.h and potESC.ino
4 |  | Enter blue highlighted items into myCLaw.h |  |  |  |  |  |  | Entry to myCLAW.h and potESC.ino; same between units
5 |  | Run the frequency response fr_
6 |  | Enter results of fr_ into table lower right corner this sheet
7 |  | Hand tune DELTAV |  |  |  |  |  |  |  |  |  |  |  |  | // Constants always defined - potESC.ino #ifdef Arduino
8 |  | Check that Nt corresponding to entry in column AG lines up with Nt from Z in Tau data |  |  |  |  |  |  |  |  |  |  |  |  | POT_MAX | 5 |  |  | v
 |  |  |  |  |  |  |  |  |  |  |  |  |  |  | F2V_MAX | 5 |  |  | v
Motor | numPoles | 1 |  |  |  |  |  | Inertia Turbine Only (need motor***) |  |  |  |  |  |  | F2V_MIN | 0 |  |  | v
 | Kv | 4800 | rpm/V |  |  |  |  | Rt= | 25 | mm |  |  |  |  | POT_MIN | 0 |  |  | v
 | Vc | 12 |  |  |  |  |  | Mt= | 2.1797 | gm |  |  |  |  | DENS_SI | 1.225 |  |  | kg/m^3
 | Ra | 0.0399 | O |  |  |  |  | Jt= | 0.001548498305 | lbm-in^2 | 1/3*MR^2
 | La | 4.2e-06 | H |  |  |  |  | Rm= | 4.8 | mm | at most |  |  |  | // See calibration<date>.xlsx - myCLAW.h
 | Power | 240 | W max |  |  |  |  | Lm= | 19.0 | mm | at most |  |  |  | RPM_P | 460.8 |  |  | rpm/%
 | Kvrps | 502.7 | r/s / V |  |  |  |  | Mm= | 0.006212622191 | lbm | at most |  |  |  | THTL_MAX | 180 |  |  | deg
 | Kt | 0.0139 | ft-lbf/A |  |  |  |  | Jm | 0.0001092062495 | lbm-in^2 | 1/2*MR^2 |  |  |  | THTL_MIN | 0 |  |  | deg
 | Fn | 0.99 | lbf |  |  |  |  | J= | 0.001657704555 | lbm-in^2 |  |  |  |  | AREA_SI | 0.002121360439 |  |  | m^2
 |  |  |  |  |  |  |  | J= | 1.151183719e-05 | lbm-ft^2 |  |  |  |  | NM_2_FTLBF | 0.738 |  |  | ft-lbf/N-m
LM2907N Circuit |  | vf2v, v |  |  |  |  |  | J= | 3.74268175e-08 | ft-lbf/(rpm/sec) |  |  |  |  | JT | 3.74268175e-08 |  |  | rpm/s / ft-lbf
 | F2V_MIN | 0 |  |  |  |  |  |  |  |  |  |  |  |  | D_SI | 0.055 |  |  | m
 | F2V_MAX | 5 |  |  |  |  |  | From fr_a1_t1_e1_g1b_t1a.xlsx |  |  |  |  |  |  | FG_SI | 4.425 |  |  | N
 |  |  |  |  |  |  |  | Nt, % | Calc Ng, % | Meas TauT1, s | Meas QdN, ft-lbf/rpm | Meas dQdN, N-m/rpm
Fan Rotor | Dia | 55 | mm |  |  |  |  | 68.3 | 82.7 | 0 |  |  |  |  | // Ard1_Turn1x_ESC1_G1b_T1a - myCLAW.h
 | Dia spinner | 18 | mm |  |  |  |  | 62 | 76.3 | 0.030 |  |  |  |  | P_V4_NT | 0 | 12959.72295 | 264.0925319 | rpm
 |  |  |  |  |  |  |  | 48 | 62.0 | 0.097 | 3.858434794e-07 | -5.230494207e-07 | cal point |  | P_LT_NG | -19322.83883 | 11482.8953 |  | rpm
Air | Dens | 1.225 | kg/m^3 | SLS Std Day |  |  |  | 25 | 38.5 | 0.287 |  |  |  |  | P_NG_NT | -5799.543768 | 0.9769 |  | rpm
 |  |  |  |  |  |  |  | 16 | 29.3 | 0.442 |  |  |  |  | P_NT_NG | 5950.435046 | 1.0229 |  | rpm
Thtl | min | 0 | V Pot |  |  |  |  | 12.6 | 25.8 | 0.5 |  |  |  |  | DCPDL | -0.830 |  |  | none
 | max | 5 | V Pot |  |  |  |  |  |  |  |  |  |  |  | LAMBDA | 3.16 |  |  | none
 | min | 0 | deg Throttle |  |  |  |  |  |  |  |  |  |  |  | DELTAV | 2 |  |  | m/s
 | max | 180 | deg Throttle |  |  |  |  | P_NG_QG | -0.002282899263 | 1.97751564e-07 | 9.326941385e-12 | ft-lbf |  |  |  |  |  |  | 12.59
Adjust | 1.25 | for 100% Ng at |  | 240 | watts |  |  | matlabTuning.xlsx |  |  |  | tldF=.15, tlgF=.03
 |  |  |  |  |  |  |  | TauT Design, s | Nt, % | TLD_S | LG_S | TLD_L | LG_L |  | xAll | 0.0 | 21.7 | 37.3 | 50.5 | 64.1 | 80.0
 |  |  |  |  |  |  |  | 0 | 68.3 | 0.2 | 4.4 | 0.09 | 5 |  | TLD_S | 0.475 | 0.475 | 0.325 | 0.225 | 0.200 | 0.200 | Scheduled
 |  |  |  |  |  |  |  | 0.02 | 64.1 | 0.2 | 3.75 | 0.09 | 5 |  | LG_S | 2.40 | 2.40 | 2.70 | 3.20 | 3.75 | 4.40
 |  |  |  |  |  |  |  | 0.085 | 50.5 | 0.225 | 3.2 | 0.125 | 4.050 |  | tldF | 0.15
 |  |  |  |  |  |  |  | 0.185 | 37.3 | 0.325 | 2.7 | 0.24 | 3.75 |  | tlgF | 0.03
 |  |  |  |  |  |  |  | 0.344 | 21.7 | 0.475 | 2.4 | 0.42 | 3.6 |  | TLD_L | 0.420 | 0.420 | 0.240 | 0.125 | 0.090 | 0.090 | Fixed lead
 |  |  |  |  |  |  |  | 0.5 | 12.6 | 0.475 | 2.4 | 0.42 | 3.6 |  | LG_L | 3.60 | 3.60 | 3.75 | 4.05 | 5.00 | 5.00
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

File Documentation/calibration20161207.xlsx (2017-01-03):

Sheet: Ard1_Turn1x_ESC1_G1b_T1a
Description | Set Nt | TTL, ms | throttleFlt, deg | v4, vdc | Charger V, vdc | Charger I, A | Tng, micros | Ttur, micros |  | Charger Pwr, W | Throttle, deg | ln(Throttle) | FreqNg, Hz | FreqTur, Hz | Ng, RPM | Nt, RPM | Ng, % | Nt, % | Throttle, deg | Charger Pwr, W | Ng Pwr, W | Ng Pwr, SHP | Ng Total Torque, ft-lbf | Ng Torque, ft-lbf | Thrust, N | Thrust Power, W | Overall Efficiency | Vw, m/s | Vw, mph | Vt, m/s | Lambda tip speed ratio | dCpdLambda | simulate vpot from throttle | model throttle from vpot | Model Ng from Model Throttle, rpm | Model Ng from Model Throttle, % | Model pcntRef from Model Ng, % | Model Ng from pcntRef at RESET, % | Model Nt from Model Ng, % | Model Nt from Model Ng, rpm | Model Qg from Model Ng, ft-lbf | Model PwrG from Model Ng*Q, shp | Model dQgdNg, ft-lbf/rpm | Model TauG | Model dQtdNt, ft-lbf/rpm | Model TauT from wind | v4, vdc
DC Power Overhead | n/a | 1.03 | 5.37 | 0.0032 | 12.24 | 0.019 | 1e+32 | 1e+32 |  | 0.2 | 5.37 | 1.6802 | 1e-26 | 1e-26 | 6e-25 | 0 | 1.302083333e-27 | 0 | 5.366686677 | 0.23 | 0 | 0.0000 | 0.00000 | 0.00000 | 9.768434808e-87 | 9.469612349e-129 |  | 1.938818764e-42 | 4.362342218e-42 | 0 | 0.00 |  | 0.149 | 5.367 | 0.00 | 0.00 | -12.58 | 0.04 |  | 0 |  |  |  |  |  |  | 0.0032
Lowest Ng | n/a | 1.04 | 8 | 0.0046 | 12.23 | 0.28 | 8000 | 1e+32 |  | 3.4 | 8 | 2.0794 | 125 | 1e-26 | 7500 | 6e-25 | 16.27604167 | 1.302083333e-27 | 8 | 3.39 | 3.15515 | 0.0042 | 0.00296 | 0.00000 | 0.019 | 0.03 | 0.8 | 2.71 | 6.1 | 1.727875959e-27 | 6.376910601e-28 |  | 0.222 | 8.000 | 4555.44 | 9.89 | -2.91 | 9.92 |  | 0 | 0.00000 | 0.00000 | 2.853062032e-07 |  |  |  | 0.0046
First Nt | tbd | 1.07 | 12 | 0.238 | 12.25 | 0.53 | 5540 | 13200 |  | 6.5 | 12 | 2.4849 | 180.5054152 | 75.75757576 | 10830.32491 | 4545.454545 | 23.50330927 | 9.864267677 | 12 | 6.47 | 6.24 | 0.0084 | 0.00405 | 0.00109 | 0.057 | 0.14 | 2.1 | 4.70 | 10.6 | 13.1 | 2.78 |  | 0.333 | 12.000 | 9182.02 | 19.93 | 6.90 | 19.95 | 6.9 | 3180.56593 | 0.00032 | 0.00055 | 3.710841217e-07 | 0.101 |  |  | 0.238
Dynamic Nt #1 | 16 | 1.09 | 17 | 0.434 | 12.24 | 0.655 | 4900 | 10000 |  | 8.0 | 17 | 2.8332 | 204.0816327 | 100 | 12244.89796 | 6000 | 26.57312925 | 13.02083333 | 17 | 8.02 | 7.78 | 0.0104 | 0.00448 | 0.00151 | 0.083 | 0.23 | 2.9 | 5.65 | 12.7 | 17.3 | 3.06 |  | 0.472 | 17.000 | 13156.38 | 28.55 | 15.33 | 28.57 | 15.3 | 7065.747639 | 0.00194 | 0.00485 | 4.447699274e-07 | 0.084 |  |  | 0.434
Dynamic Nt #2 | 20 | 1.12 | 21 | 0.586 | 12.24 | 0.877 | 4180 | 7500 |  | 10.7 | 21 | 3.0445 | 239.2344498 | 133.3333333 | 14354.06699 | 8000 | 31.15031898 | 17.36111111 | 21 | 10.73 | 10.50 | 0.0141 | 0.00515 | 0.00219 | 0.134 | 0.48 | 4.5 | 7.17 | 16.1 | 23.0 | 3.21 |  | 0.583 | 21.000 | 15567.53 | 33.78 | 20.45 | 33.80 | 20.4 | 9422.791701 | 0.00306 | 0.00908 | 4.894732912e-07 | 0.076 | -1.170331375e-07 | 0.320 | 0.586
Dynamic Nt #3 | 25 | 1.15 | 27 | 0.793 | 12.23 | 1.23 | 3540 | 5580 |  | 15.0 | 27 | 3.2958 | 282.4858757 | 179.2114695 | 16949.15254 | 10752.68817 | 36.78201507 | 23.33482676 | 27 | 15.04 | 14.81 | 0.0199 | 0.00615 | 0.00319 | 0.220 | 1.01 | 6.7 | 9.21 | 20.7 | 31.0 | 3.36 |  | 0.750 | 27.000 | 18435.17 | 40.01 | 26.53 | 40.02 | 26.5 | 12226.07466 | 0.00454 | 0.01595 | 5.426399585e-07 | 0.069 | -1.555310512e-07 | 0.241 | 0.793
Dynamic Nt #4 | 36 | 1.23 | 42 | 1.175 | 12.19 | 2.41 | 2770 | 3760 |  | 29.4 | 42 | 3.7377 | 361.0108303 | 265.9574468 | 21660.64982 | 15957.44681 | 47.00661853 | 34.62987589 | 42 | 29.38 | 29.15 | 0.0391 | 0.00948 | 0.00651 | 0.460 | 3.06 | 10.4 | 13.30 | 29.9 | 46.0 | 3.46 |  | 1.167 | 42.000 | 23476.72 | 50.95 | 37.23 | 50.95 | 37.2 | 17154.49135 | 0.00751 | 0.03359 | 6.361116112e-07 | 0.059 | -2.331294905e-07 | 0.161 | 1.175
Dynamic Nt #5 | 45 | 1.37 | 67 | 1.624 | 12.13 | 4.27 | 2170 | 2810 |  | 51.8 | 67 | 4.2047 | 460.8294931 | 355.8718861 | 27649.76959 | 21352.31317 | 60.00384025 | 46.33748517 | 67 | 51.80 | 51.56 | 0.0691 | 0.01313 | 0.01017 | 0.956 | 9.17 | 17.7 | 19.18 | 43.2 | 61.5 | 3.206 |  | 1.861 | 67.000 | 28805.70 | 62.51 | 48.53 | 62.51 | 48.5 | 22363.8923 | 0.01117 | 0.06125 | 7.349123714e-07 | 0.051 | -3.446051705e-07 | 0.109 | 1.624
Dynamic Nt #6 | 50 | 1.39 | 70 | 1.652 | 12.12 | 4.5 | 2140 | 2750 |  | 54.5 | 70 | 4.2485 | 467.2897196 | 363.6363636 | 28037.38318 | 21818.18182 | 60.84501558 | 47.34848485 | 70 | 54.54 | 54.31 | 0.0728 | 0.01364 | 0.01068 | 0.997 | 9.76 | 17.9 | 19.58 | 44.1 | 62.8 | 3.208 |  | 1.944 | 70.000 | 29305.51 | 63.60 | 49.59 | 63.59 | 49.6 | 22852.48798 | 0.01154 | 0.06437 | 7.441790079e-07 | 0.050 | -3.522768629e-07 | 0.106 | 1.652
Dynamic Nt #7 | 52 | 1.44 | 79 | 1.786 | 12.09 | 5.32 | 2020 | 2560 |  | 64.3 | 79 | 4.3694 | 495.049505 | 390.625 | 29702.9703 | 23437.5 | 64.45957096 | 50.86263021 | 79 | 64.32 | 64.09 | 0.0859 | 0.01520 | 0.01223 | 1.185 | 12.65 | 19.7 | 21.36 | 48.0 | 67.5 | 3.161 | -0.789 | 2.194 | 79.000 | 30685.65 | 66.59 | 52.52 | 66.58 | 52.5 | 24201.65203 | 0.01258 | 0.07351 | 7.697670621e-07 | 0.049 | -3.858434794e-07 | 0.097 | 1.786
Dynamic Nt #8 | 55 | 1.47 | 84 | 1.842 | 12.08 | 5.63 | 1970 | 2480 |  | 68.0 | 84 | 4.4308 | 507.6142132 | 403.2258065 | 30456.85279 | 24193.54839 | 66.09560068 | 52.50336022 | 84 | 68.01 | 67.78 | 0.0909 | 0.01567 | 0.01271 | 1.278 | 14.17 | 20.8 | 22.17 | 49.9 | 69.7 | 3.142 |  | 2.333 | 84.000 | 31385.90 | 68.11 | 54.01 | 68.10 | 54.0 | 24886.19101 | 0.01313 | 0.07844 | 7.827499313e-07 | 0.048 | -4.013519742e-07 | 0.093 | 1.842
Dynamic Nt #8 | 62 | 1.67 | 121 | 2.19 | 11.97 | 8.66 | 1650 | 2040 |  | 103.7 | 121 | 4.7958 | 606.0606061 | 490.1960784 | 36363.63636 | 29411.76471 | 78.91414141 | 63.82761438 | 121 | 103.66 | 103.43 | 0.1387 | 0.02003 | 0.01707 | 2.175 | 31.45 | 30.3 | 28.93 | 65.1 | 84.7 | 2.928 |  | 3.361 | 121.000 | 35550.45 | 77.15 | 62.84 | 77.13 | 62.8 | 28957.2851 | 0.01655 | 0.11200 | 8.59961725e-07 | 0.044 | -5.293725584e-07 | 0.071 | 2.19
Max | tbd | 1.97 | 175 | 2.66 | 11.7 | 14.72 | 1360 | 1620 |  | 172.2 | 175 | 5.1648 | 735.2941176 | 617.2839506 | 44117.64706 | 37037.03704 | 95.74142157 | 80.3755144 | 175 | 172.22 | 171.99 | 0.2306 | 0.02746 | 0.02449 | 4.425 | 91.30 | 53.0 | 41.26 | 92.8 | 106.7 | 2.585 |  | 4.861 | 175.000 | 39760.89 | 86.29 | 71.77 | 86.26 | 71.8 | 33073.23897 | 0.02033 | 0.15392 | 9.380243231e-07 | 0.040 | -7.632271006e-07 | 0.049 | 2.66
Calibration sheet
1 |  | Calibrate the ESC first |  |  |  |  |  | Key | User Inputs
2 |  | Update the Arduino software |  |  |  |  |  |  | Derived
3 |  | Run the points below |  |  |  |  |  |  | Entry to myCLAW.h and potESC.ino
4 |  | Enter blue highlighted items into myCLaw.h |  |  |  |  |  |  | Entry to myCLAW.h and potESC.ino; same between units
5 |  | Run the frequency response fr_
6 |  | Enter results of fr_ into table lower right corner this sheet
7 |  | Hand tune DELTAV |  |  |  |  |  |  |  |  |  |  |  |  | // Constants always defined - potESC.ino #ifdef Arduino
8 |  | Check that Nt corresponding to entry in column AG lines up with Nt from Z in Tau data |  |  |  |  |  |  |  |  |  |  |  |  | POT_MAX | 5 |  |  | v
 |  |  |  |  |  |  |  |  |  |  |  |  |  |  | F2V_MAX | 5 |  |  | v
Motor | numPoles | 1 |  |  |  |  |  | Inertia Turbine Only (need motor***) |  |  |  |  |  |  | F2V_MIN | 0 |  |  | v
 | Kv | 4800 | rpm/V |  |  |  |  | Rt= | 25 | mm |  |  |  |  | POT_MIN | 0 |  |  | v
 | Vc | 12 |  |  |  |  |  | Mt= | 2.1797 | gm |  |  |  |  | DENS_SI | 1.225 |  |  | kg/m^3
 | Ra | 0.0399 | O |  |  |  |  | Jt= | 0.001548498305 | lbm-in^2 | 1/3*MR^2
 | La | 4.2e-06 | H |  |  |  |  | Rm= | 4.8 | mm | at most |  |  |  | // See calibration<date>.xlsx - myCLAW.h
 | Power | 240 | W max |  |  |  |  | Lm= | 19.0 | mm | at most |  |  |  | RPM_P | 460.8 |  |  | rpm/%
 | Kvrps | 502.7 | r/s / V |  |  |  |  | Mm= | 0.006212622191 | lbm | at most |  |  |  | THTL_MAX | 180 |  |  | deg
 | Kt | 0.0139 | ft-lbf/A |  |  |  |  | Jm | 0.0001092062495 | lbm-in^2 | 1/2*MR^2 |  |  |  | THTL_MIN | 0 |  |  | deg
 | Fn | 0.99 | lbf |  |  |  |  | J= | 0.001657704555 | lbm-in^2 |  |  |  |  | AREA_SI | 0.002121360439 |  |  | m^2
 |  |  |  |  |  |  |  | J= | 1.151183719e-05 | lbm-ft^2 |  |  |  |  | NM_2_FTLBF | 0.738 |  |  | ft-lbf/N-m
LM2907N Circuit |  | vf2v, v |  |  |  |  |  | J= | 3.74268175e-08 | ft-lbf/(rpm/sec) |  |  |  |  | JT | 3.74268175e-08 |  |  | rpm/s / ft-lbf
 | F2V_MIN | 0 |  |  |  |  |  |  |  |  |  |  |  |  | D_SI | 0.055 |  |  | m
 | F2V_MAX | 5 |  |  |  |  |  | From fr_a1_t1_e1_g1b_t1a.xlsx |  |  |  |  |  |  | FG_SI | 4.425 |  |  | N
 |  |  |  |  |  |  |  | Nt, % | Calc Ng, % | Meas TauT1, s | Meas QdN, ft-lbf/rpm | Meas dQdN, N-m/rpm
Fan Rotor | Dia | 55 | mm |  |  |  |  | 68.3 | 82.7 | 0 |  |  |  |  | // Ard1_Turn1x_ESC1_G1b_T1a - myCLAW.h
 | Dia spinner | 18 | mm |  |  |  |  | 62 | 76.3 | 0.030 |  |  |  |  | P_V4_NT | 0 | 12893.70975 | 287.5020511 | rpm
 |  |  |  |  |  |  |  | 48 | 62.0 | 0.097 | 3.858434794e-07 | -5.230494207e-07 | cal point |  | P_LT_NG | -19172.11148 | 11410.53997 |  | rpm
Air | Dens | 1.225 | kg/m^3 | SLS Std Day |  |  |  | 25 | 38.5 | 0.287 |  |  |  |  | P_NG_NT | -5795.402634 | 0.9776 |  | rpm
 |  |  |  |  |  |  |  | 16 | 29.3 | 0.442 |  |  |  |  | P_NT_NG | 5943.033349 | 1.0222 |  | rpm
Thtl | min | 0 | V Pot |  |  |  |  | 12.6 | 25.8 | 0.5 |  |  |  |  | DCPDL | -0.789 |  |  | none
 | max | 5 | V Pot |  |  |  |  |  |  |  |  |  |  |  | LAMBDA | 3.16 |  |  | none
 | min | 0 | deg Throttle |  |  |  |  |  |  |  |  |  |  |  | DELTAV | 1 |  |  | m/s
 | max | 180 | deg Throttle |  |  |  |  | P_NG_QG | -0.002310471263 | 2.008471737e-07 | 9.270129978e-12 | ft-lbf
Adjust | 1.25 | for 100% Ng at |  | 240 | watts |  |  | matlabTuning.xlsx |  |  |  | tldF=.15, tlgF=.03
 |  |  |  |  |  |  |  | TauT Design, s | Nt, % | TLD_S | LG_S | TLD_L | LG_L |  | xAll | 0.0 | 21.7 | 37.3 | 50.5 | 64.1 | 80.0
 |  |  |  |  |  |  |  | 0 | 68.3 | 0.2 | 4.4 | 0.09 | 5 |  | TLD_S | 0.475 | 0.475 | 0.325 | 0.225 | 0.200 | 0.200 | Scheduled
 |  |  |  |  |  |  |  | 0.02 | 64.1 | 0.2 | 3.75 | 0.09 | 5 |  | LG_S | 2.40 | 2.40 | 2.70 | 3.20 | 3.75 | 4.40
 |  |  |  |  |  |  |  | 0.085 | 50.5 | 0.225 | 3.2 | 0.125 | 4.050 |  | tldF | 0.15
 |  |  |  |  |  |  |  | 0.185 | 37.3 | 0.325 | 2.7 | 0.24 | 3.75 |  | tlgF | 0.03
 |  |  |  |  |  |  |  | 0.344 | 21.7 | 0.475 | 2.4 | 0.42 | 3.6 |  | TLD_L | 0.420 | 0.420 | 0.240 | 0.125 | 0.090 | 0.090 | Fixed lead
 |  |  |  |  |  |  |  | 0.5 | 12.6 | 0.475 | 2.4 | 0.42 | 3.6 |  | LG_L | 3.60 | 3.60 | 3.75 | 4.05 | 5.00 | 5.00

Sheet: Ard2_Turn2_ESC2_G2b_T2a
Description | Set Nt | TTL, ms | throttleFlt, deg | v4, vdc | Charger V, vdc | Charger I, A | Tng, micros | Ttur, micros |  | Charger Pwr, W | Throttle, deg | ln(Throttle) | FreqNg, Hz | FreqTur, Hz | Ng, RPM | Nt, RPM | Ng, % | Nt, % | Throttle, deg | Charger Pwr, W | Ng Pwr, W | Ng Pwr, SHP | Ng Total Torque, ft-lbf | Ng Torque, ft-lbf | Thrust, N | Thrust Power, W | Overall Efficiency | Vw, m/s | Vw, mph | Vt, m/s | Lambda tip speed ratio | dCpdLambda | simulate vpot from throttle | model throttle from vpot | Model Ng from Model Throttle, rpm | Model Ng from Model Throttle, % | Model pcntRef from Model Ng, % | Model Ng from pcntRef at RESET, % | Model Nt from Model Ng, % | Model Nt from Model Ng, rpm | Model Qg from Model Ng, ft-lbf | Model PwrG from Model Ng*Q, shp | Model dQgdNg, ft-lbf/rpm | Model TauG | Model dQtdNt, ft-lbf/rpm | Model TauT from wind
DC Power Overhead | n/a | 1.00 | 0.00 | 0.0034 | 12.22 | 0.051 | 1e+32 | 1e+32 |  | 0.6 | 0.00 | #NUM! | 1e-26 | 1e-26 | 6e-25 | 0 | 1.302083333e-27 | 0 | 0 | 0.62 | 0 | 0.0000 | 0.00000 | 0.00000 | 9.768434808e-87 | 9.469612349e-129 |  | 1.938818764e-42 | 4.362342218e-42 | 0 | 0.00 |  | 0.000 | 0.000 | #NUM! | #NUM! | #NUM! | #NUM! |  | #NUM!
Lowest Ng | n/a | 1.07 | 13 | 0.113 | 12.2 | 0.43 | 5740 | 1e+32 |  | 5.3 | 13 | 2.5649 | 174.2160279 | 1e-26 | 10452.96167 | 6e-25 | 22.68437863 | 1.302083333e-27 | 13 | 5.29 | 4.67158 | 0.0063 | 0.00315 | 0.00000 | 0.052 | 0.12 | 2.2 | 4.46 | 10.0 | 1.727875959e-27 | 3.875637832e-28 |  | 0.361 | 13.000 | 6325.87 | 13.73 | -0.17 | 13.82 |  | 0 | 0.00000 | 0.00000 | 2.296887944e-07
First Nt | tbd | 1.09 | 17 | 0.303 | 12.2 | 0.44 | 5660 | 16300 |  | 5.4 | 17 | 2.8332 | 176.6784452 | 61.34969325 | 10600.70671 | 3680.981595 | 23.00500589 | 7.988241309 | 17 | 5.37 | 4.74 | 0.0064 | 0.00315 | 4.764105173e-06 | 0.054 | 0.12 | 2.3 | 4.55 | 10.2 | 10.6 | 2.33 |  | 0.472 | 17.000 | 9776.53 | 21.22 | 6.93 | 21.29 | 6.9 | 3193.923653 | 0.00000 | 0.00000 | 3.012018229e-07 | 0.124
Dynamic Nt #1 | 16 | 1.13 | 24 | 0.285 | 12.19 | 0.838 | 4220 | 8180 |  | 10.2 | 24 | 3.1781 | 236.9668246 | 122.2493888 | 14218.00948 | 7334.963325 | 30.85505529 | 15.91788916 | 24 | 10.22 | 9.59 | 0.0129 | 0.00475 | 0.00160 | 0.130 | 0.46 | 4.5 | 7.07 | 15.9 | 21.1 | 2.99 |  | 0.667 | 24.000 | 14212.19 | 30.84 | 16.07 | 30.90 | 16.1 | 7403.02921 | 0.00138 | 0.00373 | 3.931283907e-07 | 0.095
Dynamic Nt #2 | 20 | 1.16 | 28 | 0.449 | 12.18 | 0.981 | 3750 | 6520 |  | 11.9 | 28 | 3.3322 | 266.6666667 | 153.3742331 | 16000 | 9202.453988 | 34.72222222 | 19.97060327 | 28 | 11.95 | 11.33 | 0.0152 | 0.00499 | 0.00184 | 0.185 | 0.78 | 6.5 | 8.44 | 19.0 | 26.5 | 3.14 |  | 0.778 | 28.000 | 16195.02 | 35.15 | 20.15 | 35.19 | 20.1 | 9284.584621 | 0.00220 | 0.00678 | 4.342214279e-07 | 0.086 | -9.741432305e-08 | 0.384
Dynamic Nt #3 | 25 | 1.18 | 32 | 0.576 | 12.17 | 1.359 | 3370 | 5480 |  | 16.5 | 32 | 3.4657 | 296.735905 | 182.4817518 | 17804.1543 | 10948.90511 | 38.63748764 | 23.76064477 | 32 | 16.54 | 15.92 | 0.0213 | 0.00630 | 0.00315 | 0.255 | 1.26 | 7.6 | 9.91 | 22.3 | 31.5 | 3.18 |  | 0.889 | 32.000 | 17912.63 | 38.87 | 23.69 | 38.91 | 23.7 | 10914.46205 | 0.00297 | 0.01014 | 4.698178358e-07 | 0.080 | -1.389379631e-07 | 0.269
Dynamic Nt #4 | 36 | 1.28 | 50 | 1.323 | 12.13 | 2.6 | 2510 | 3620 |  | 31.5 | 50 | 3.9120 | 398.4063745 | 276.2430939 | 23904.38247 | 16574.58564 | 51.87583001 | 35.96915285 | 50 | 31.54 | 30.91 | 0.0415 | 0.00911 | 0.00596 | 0.618 | 4.76 | 15.1 | 15.42 | 34.7 | 47.7 | 3.10 |  | 1.389 | 50.000 | 23653.19 | 51.33 | 35.51 | 51.34 | 35.5 | 16361.81989 | 0.00601 | 0.02708 | 5.887877457e-07 | 0.064 | -2.947704497e-07 | 0.127
Dynamic Nt #5 | 45 | 1.43 | 78 | 1.685 | 12.07 | 4.32 | 2120 | 2800 |  | 52.1 | 78 | 4.3567 | 471.6981132 | 357.1428571 | 28301.88679 | 21428.57143 | 61.41902516 | 46.50297619 | 78 | 52.14 | 51.52 | 0.0691 | 0.01282 | 0.00967 | 1.025 | 10.18 | 19.5 | 19.86 | 44.7 | 61.7 | 3.107 | -1.158 | 2.167 | 78.000 | 29373.16 | 63.74 | 47.29 | 63.73 | 47.3 | 21789.63256 | 0.00972 | 0.05436 | 7.073307907e-07 | 0.053 | -4.205260394e-07 | 0.089
Dynamic Nt #6 | 50 | 1.64 | 115 | 1.892 | 11.99 | 6 | 1760 | 2380 |  | 71.9 | 115 | 4.7449 | 568.1818182 | 420.1680672 | 34090.90909 | 25210.08403 | 73.98200758 | 54.70938375 | 115 | 71.94 | 71.32 | 0.0956 | 0.01473 | 0.01159 | 1.792 | 23.52 | 32.7 | 26.26 | 59.1 | 72.6 | 2.765 |  | 3.194 | 115.000 | 34366.85 | 74.58 | 57.57 | 74.54 | 57.6 | 26528.26657 | 0.01351 | 0.08840 | 8.108222225e-07 | 0.046 | -6.014952372e-07 | 0.062
Dynamic Nt #7 | 52 | 1.78 | 140 | 2.02 | 11.97 | 7.13 | 1750 | 2210 |  | 85.3 | 140 | 4.9416 | 571.4285714 | 452.4886878 | 34285.71429 | 27149.32127 | 74.4047619 | 58.91779789 | 140 | 85.35 | 84.72 | 0.1136 | 0.01740 | 0.01426 | 1.823 | 24.14 | 28.3 | 26.48 | 59.6 | 78.2 | 2.952 |  | 3.889 | 140.000 | 36897.12 | 80.07 | 62.78 | 80.02 | 62.8 | 28929.30248 | 0.01563 | 0.10979 | 8.632606771e-07 | 0.043 | -6.0787262e-07 | 0.062
Dynamic Nt #8 | 55 | 1.86 | 155 | 2.14 | 11.91 | 8.5 | 1620 | 2070 |  | 101.2 | 155 | 5.0434 | 617.2839506 | 483.0917874 | 37037.03704 | 28985.50725 | 80.3755144 | 62.90257649 | 155 | 101.23 | 100.61 | 0.1349 | 0.01913 | 0.01598 | 2.298 | 34.16 | 33.7 | 29.73 | 66.9 | 83.5 | 2.807 |  | 4.306 | 155.000 | 38206.34 | 82.91 | 65.48 | 82.86 | 65.5 | 30171.65691 | 0.01678 | 0.12204 | 8.9039361e-07 | 0.042 | -6.998576012e-07 | 0.053
Max | tbd | 1.97 | 175 | 2.67 | 11.66 | 13.84 | 1360 | 1680 |  | 161.4 | 175 | 5.1648 | 735.2941176 | 595.2380952 | 44117.64706 | 35714.28571 | 95.74142157 | 77.50496032 | 175 | 161.37 | 160.75 | 0.2156 | 0.02566 | 0.02252 | 4.425 | 91.30 | 56.6 | 41.26 | 92.8 | 102.8 | 2.492 |  | 4.861 | 175.000 | 39767.40 | 86.30 | 68.69 | 86.24 | 68.7 | 31652.9814 | 0.01819 | 0.13774 | 9.227456321e-07 | 0.041 | -1.026091681e-06 | 0.036
Calibration sheet
1 |  | Calibrate the ESC first |  |  |  |  |  | Key | User Inputs
2 |  | Update the Arduino software |  |  |  |  |  |  | Derived
3 |  | Run the points below |  |  |  |  |  |  | Entry to myCLAW.h and potESC.ino
4 |  | Enter blue highlighted items into myCLaw.h |  |  |  |  |  |  | Entry to myCLAW.h and potESC.ino; same between units
5 |  | Run the frequency response fr_
6 |  | Enter results of fr_ into table lower right corner this sheet
7 |  | Hand tune DELTAV |  |  |  |  |  |  |  |  |  |  |  |  | // Constants always defined - potESC.ino #ifdef Arduino
8 |  | Check that Nt corresponding to entry in column AG lines up with Nt from Z in Tau data |  |  |  |  |  |  |  |  |  |  |  |  | POT_MAX | 5 |  |  | v
 |  |  |  |  |  |  |  |  |  |  |  |  |  |  | F2V_MAX | 5 |  |  | v
Motor | numPoles | 1 |  |  |  |  |  | Inertia Turbine Only (need motor***) |  |  |  |  |  |  | F2V_MIN | 0 |  |  | v
 | Kv | 4800 | rpm/V |  |  |  |  | Rt= | 25 | mm |  |  |  |  | POT_MIN | 0 |  |  | v
 | Vc | 12 |  |  |  |  |  | Mt= | 2.1797 | gm |  |  |  |  | DENS_SI | 1.225 |  |  | kg/m^3
 | Ra | 0.0399 | O |  |  |  |  | Jt= | 0.001548498305 | lbm-in^2 | 1/3*MR^2
 | La | 4.2e-06 | H |  |  |  |  | Rm= | 4.8 | mm | at most |  |  |  | // See calibration<date>.xlsx - myCLAW.h
 | Power | 240 | W max |  |  |  |  | Lm= | 19.0 | mm | at most |  |  |  | RPM_P | 460.8 |  |  | rpm/%
 | Kvrps | 502.7 | r/s / V |  |  |  |  | Mm= | 0.006212622191 | lbm | at most |  |  |  | THTL_MAX | 180 |  |  | deg
 | Kt | 0.0139 | ft-lbf/A |  |  |  |  | Jm | 0.0001092062495 | lbm-in^2 | 1/2*MR^2 |  |  |  | THTL_MIN | 0 |  |  | deg
 | Fn | 0.99 | lbf |  |  |  |  | J= | 0.001657704555 | lbm-in^2 |  |  |  |  | AREA_SI | 0.002121360439 |  |  | m^2
 |  |  |  |  |  |  |  | J= | 1.151183719e-05 | lbm-ft^2 |  |  |  |  | NM_2_FTLBF | 0.738 |  |  | ft-lbf/N-m
LM2907N Circuit |  | vf2v, v |  |  |  |  |  | J= | 3.74268175e-08 | ft-lbf/(rpm/sec) |  |  |  |  | JT | 3.74268175e-08 |  |  | rpm/s / ft-lbf
 | F2V_MIN | 0 |  |  |  |  |  |  |  |  |  |  |  |  | D_SI | 0.055 |  |  | m
 | F2V_MAX | 5 |  |  |  |  |  | From fr_a2_t2_e2_g2b_t2a.xlsx |  |  |  |  |  |  | FG_SI | 4.425 |  |  | N
 |  |  |  |  |  |  |  | Nt, % | Calc Ng, % | Meas TauT2, s | Meas QdN, ft-lbf/rpm | Meas dQdN, N-m/rpm
Fan Rotor | Dia | 55 | mm |  |  |  |  | 73.4 | 91.2 | 0 |  |  |  |  | // Ard2_Turn2_ESC2_G2b_T2a - myCLAW.h
 | Dia spinner | 18 | mm |  |  |  |  | 62 | 79.2 | 0.040 |  |  |  |  | P_V4_NT | 0 | 15137.7829 | -814.3490869 | rpm
 |  |  |  |  |  |  |  | 48 | 64.5 | 0.089 | 4.205260394e-07 | -5.70065099e-07 | cal point |  | P_LT_NG | -26666.90654 | 12862.93533 |  | rpm
Air | Dens | 1.225 | kg/m^3 | SLS Std Day |  |  |  | 25 | 40.3 | 0.281 |  |  |  |  | P_NG_NT | -6083.264694 | 0.9489 |  | rpm
 |  |  |  |  |  |  |  | 20 | 35.0 | 0.386 |  |  |  |  | P_NT_NG | 6452.123032 | 1.0516 |  | rpm
Thtl | min | 0 | V Pot |  |  |  |  | 14.6 | 29.3 | 0.5 |  |  |  |  | DCPDL | -1.158 |  |  | none
 | max | 5 | V Pot |  |  |  |  |  |  |  |  |  |  |  | LAMBDA | 3.11 |  |  | none
 | min | 0 | deg Throttle |  |  |  |  |  |  |  |  |  |  |  | DELTAV | 5 |  |  | m/s
 | max | 180 | deg Throttle |  |  |  |  | P_NG_QG | -0.002116799154 | 9.858868535e-08 | 1.036221776e-11 | ft-lbf
Adjust | 1.25 | for 100% Ng at |  | 240 | watts |  |  | matlabTuning.xlsx |  |  |  | tldF=.15, tlgF=.03
 |  |  |  |  |  |  |  | TauT Design, s | Nt, % | TLD_S | LG_S | TLD_L | LG_L |  | xAll | 0.0 | 22.0 | 36.5 | 49.1 | 67.7 | 80.0
 |  |  |  |  |  |  |  | 0 | 73.4 | 0.2 | 4.4 | 0.09 | 5 |  | TLD_S | 0.475 | 0.475 | 0.325 | 0.225 | 0.200 | 0.200 | Scheduled
 |  |  |  |  |  |  |  | 0.02 | 67.7 | 0.2 | 3.75 | 0.09 | 5 |  | LG_S | 2.40 | 2.40 | 2.70 | 3.20 | 3.75 | 4.40
 |  |  |  |  |  |  |  | 0.085 | 49.1 | 0.225 | 3.2 | 0.125 | 4.050 |  | tldF | 0.15
 |  |  |  |  |  |  |  | 0.185 | 36.5 | 0.325 | 2.7 | 0.24 | 3.75 |  | tlgF | 0.03
 |  |  |  |  |  |  |  | 0.344 | 22.0 | 0.475 | 2.4 | 0.42 | 3.6 |  | TLD_L | 0.420 | 0.420 | 0.240 | 0.125 | 0.090 | 0.090 | Fixed lead
 |  |  |  |  |  |  |  | 0.5 | 14.6 | 0.475 | 2.4 | 0.42 | 3.6 |  | LG_L | 3.60 | 3.60 | 3.75 | 4.05 | 5.00 | 5.00
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

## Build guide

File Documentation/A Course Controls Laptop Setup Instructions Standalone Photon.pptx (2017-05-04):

## A-Course Controls Assignment “Controlling in the Wind” Photon Toolchain

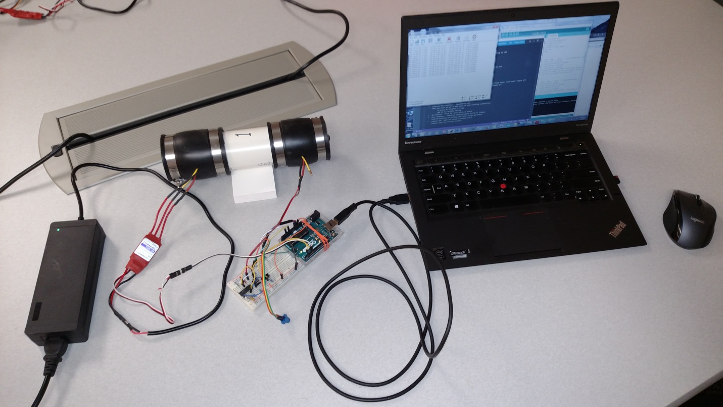
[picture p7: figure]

Dave Gutz
April 2017

## Summary

- This installs utilities and drivers to compile Photon firmware and applications completely offline. It appears to not interfere with the normal particle cli process.

## Step 0: Install link shell extension (LSE)

Makes it easy to modify Arduino code

- Link to download:
- http://download.cnet.com/Link-Shell-Extension-64-bit/3000-2248_4-75213087.html
- Link to manual:
- http://www.howtogeek.com/howto/16226/complete-guide-to-symbolic-links-symlinks-on-windows-or-linux/

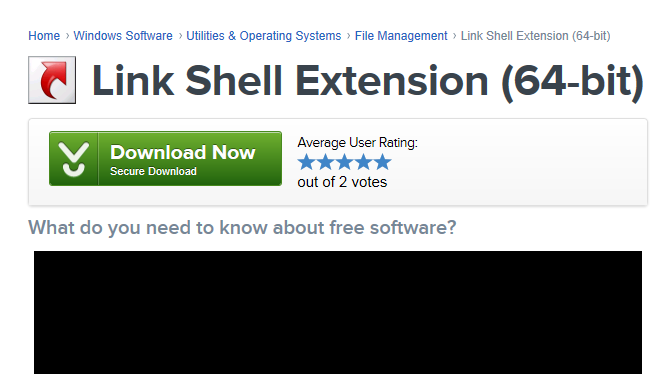
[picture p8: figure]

Click here. It will make you restart explorer.

## Reference Guide

- https://learn.sparkfun.com/tutorials/photon-development-guide/all

Scroll down to ARM GCC and DFU Bootloader (Offline) for reference....

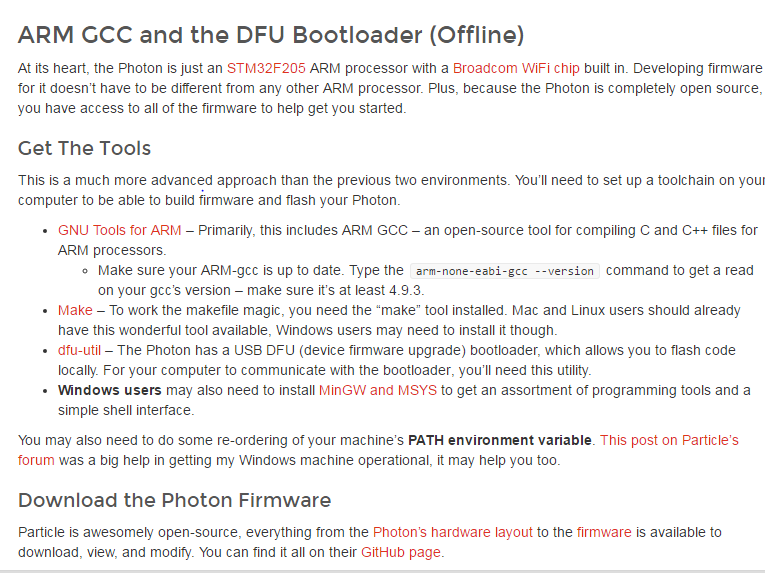
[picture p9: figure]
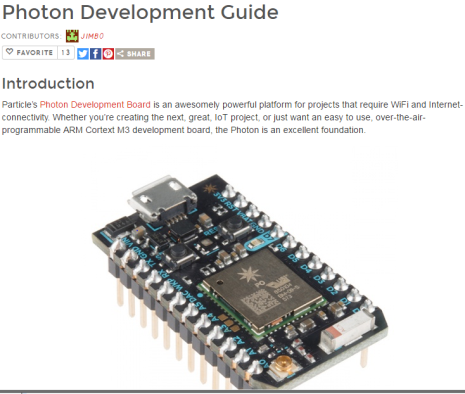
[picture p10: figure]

The following pages step through the setup of this offline process

## Step 1: Install GNU Tools for ARM

- Link to download:
- https://launchpad.net/gcc-arm-embedded

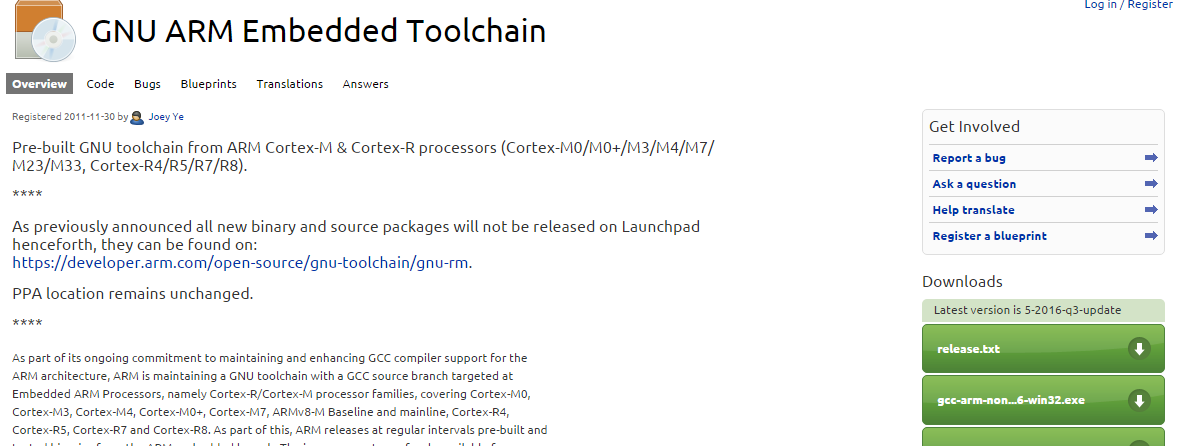
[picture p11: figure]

Needed to compile Photon

Click “Windows installer for admin install”

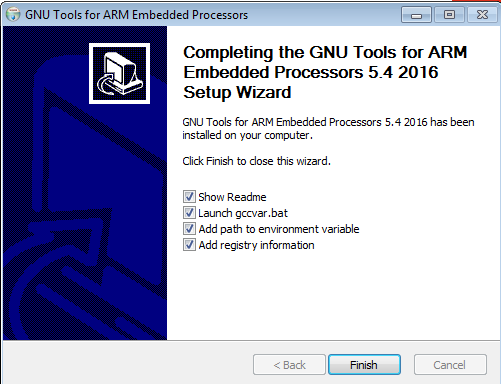
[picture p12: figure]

Close this window by “X” ing it.

Click “Add path to environment variable”

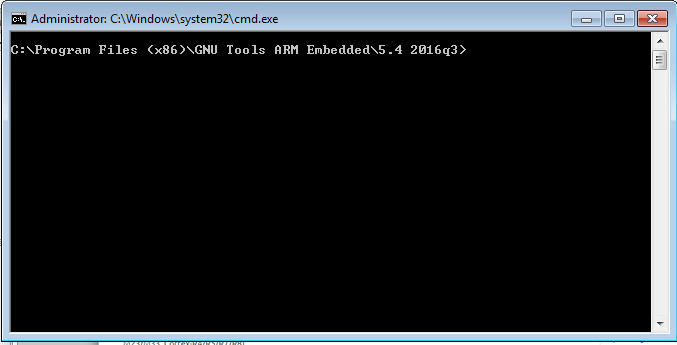
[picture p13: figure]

## Step 2: Install Make for Windows

Needed to connect compiler to code

http://gnuwin32.sourceforge.net/packages/make.htm

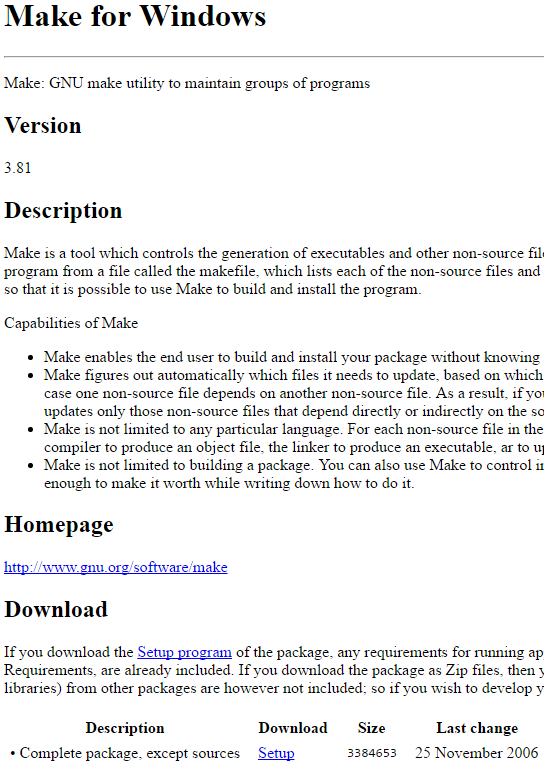
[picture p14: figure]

Click “Setup” to download make-3.81.exe. Run as admin. Full installation, all defaults.

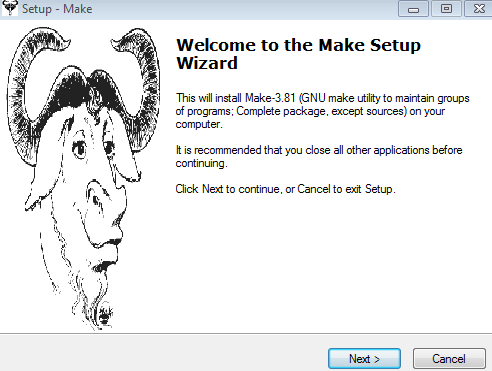
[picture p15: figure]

Successful install will finish without any notifications

## Step 3: Install dfu-util

?? Not sure this was even unzipped on laptop ??

Needed to talk to Photon

http://dfu-util.sourceforge.net/

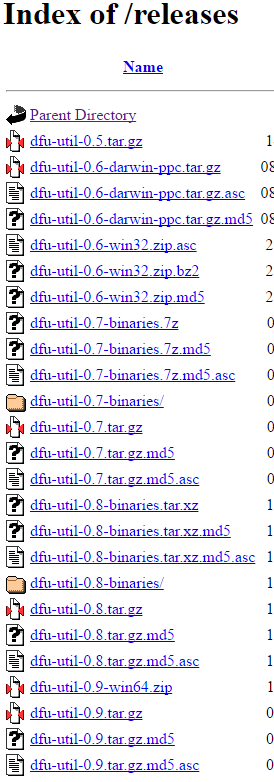
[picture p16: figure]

Click “dfu-util-0.9-win64.zip”

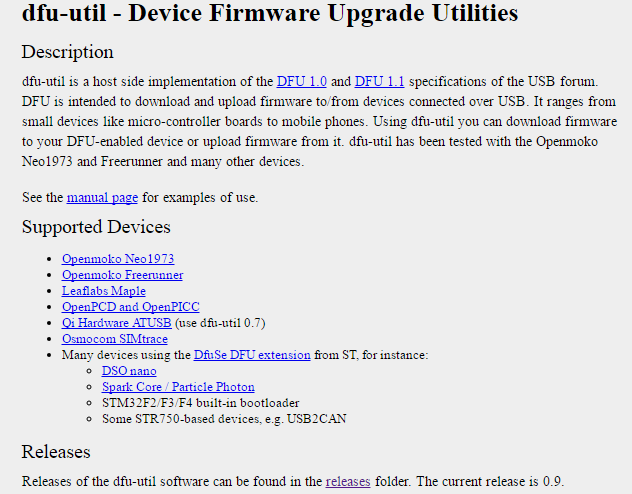
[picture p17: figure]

Click “releases”

## Step 4: Install MinGW

https://community.particle.io/t/toolchain-windows/11635

Windows Command Line Tools

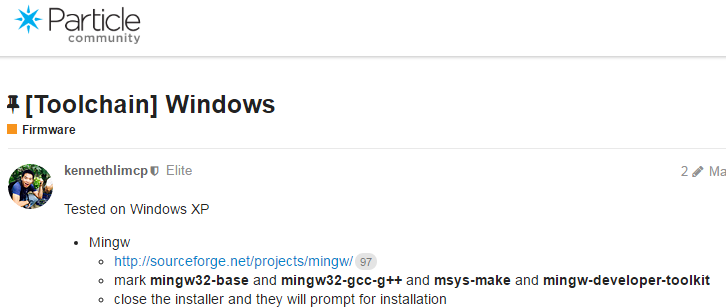
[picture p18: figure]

Click “mingw” link

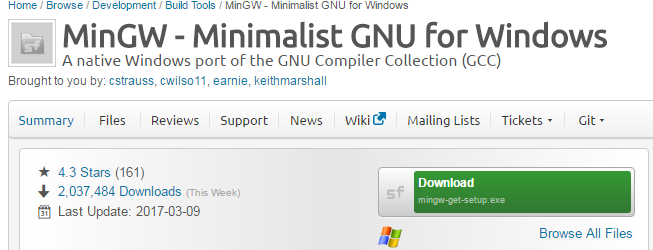
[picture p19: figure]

Click “download” for mingw-get-setup.exe. Open; all defaults.

Mark these 4 for installation.
Installation-Apply Changes
Then quit

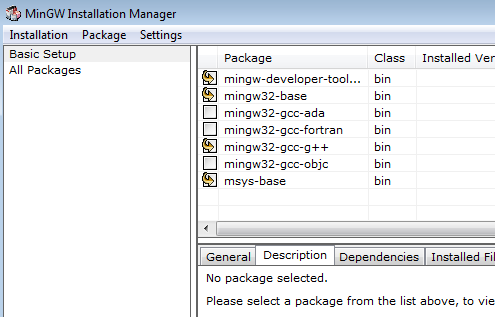
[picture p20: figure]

## Step 5: Modify Path in System Environment Variables

Windows Command Line Tools

C:\Program Files (x86)\GNU Tools ARM Embedded\4.9 2015q1\bin;C:\MinGW;C:\Program Files (x86)\GnuWin32\bin;C:\MinGW\msys\1.0\bin

original:

C:\Program Files (x86)\CVSNT\;C:\Users\210023782\AppData\Local\particle\bin;C:\Users\210023782\AppData\Local\particledev\bin;C:\Program Files (x86)\Microsoft VS Code\bin;C:\Program Files (x86)\GNU Tools ARM Embedded\5.4 2016q3\bin;C:\Program Files (x86)\GnuWin32\bin;C:\MinGW\msys\1.0\bin;C:\Git\bin
On win10 (SEE NEXT PAGE)
C:\Particle\Tools\Git\bin

Latest:

## Windows 10 PATH

C:\Program Files (x86)\GNU Tools ARM Embedded\5.4 2016q3\bin
C:\Users\Dave\AppData\Local\particle\bin
C:\Users\Dave\AppData\Roaming\npm
C:\Particle\Toolchain\Make\bin
C:\Particle\Toolchain\MinGW
C:\Particle\Toolchain\MinGW\msys\1.0\bin
C:\Particle\Toolchain\GCC-ARM\bin
C:\Particle\Tools\DFU-util
C:\dfu-util-0.8-binaries\win32-mingw32
C:\Users\Dave\AppData\Local\Microsoft\WindowsApps
C:\Program Files (x86)\Microsoft VS Code\bin
C:\Users\Dave\AppData\Local\atom\bin
C:\Program Files (x86)\GnuWin32\bin
C:\MinGW\msys\1.0\bin
C:\Particle\Tools\Git\bin

## Step 6: Install Particle Firmware

https://github.com/spark/firmware

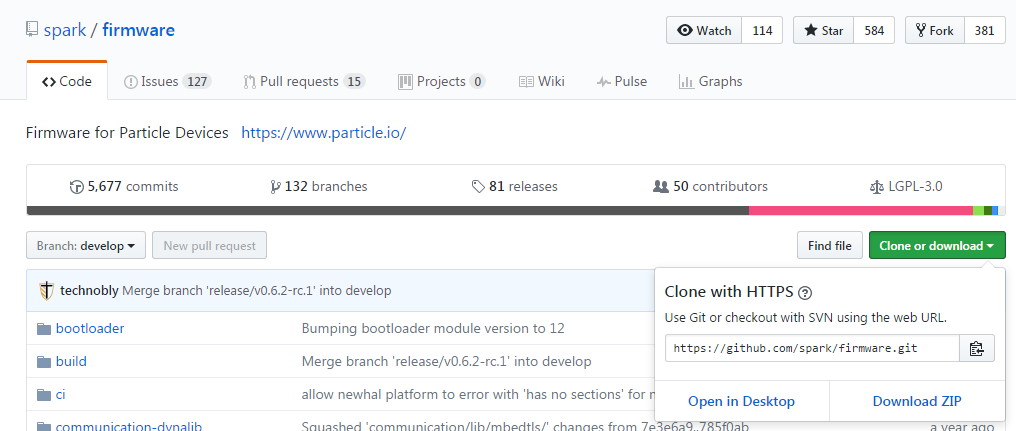
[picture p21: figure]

Get the latest

Click “Download ZIP”

Extract to GitHub Folder

If cloning get latest “release”
I got branch: “release/v0.6.2”
Xxx
“develop”

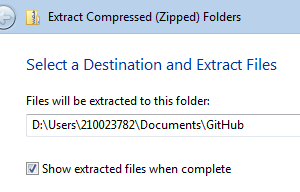
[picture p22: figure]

## Step 7: Install CoolTerm USB

- Link to install: http://freeware.the-meiers.org/CoolTerm_Win.zip

Unzip and copy “CoolTerm_0.stc” in this folder to the desktop for easy starting of USB

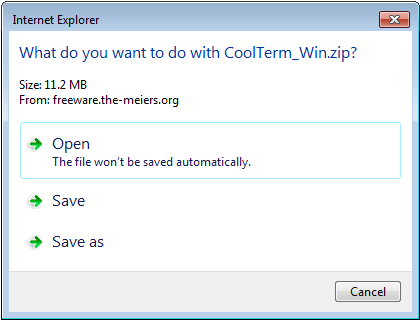
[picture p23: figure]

## Step 8: Make Firmware

- Open cmd.exe as Administrator:
cd “Users\210023782\Documents\GitHub\firmware\main”
Or
cd “C:\Users\<name>\Documents\GitHub\firmware-develop\main” #for Win10
make clean all v=1

***If command not found, PATH not correct. Correct and restart cmd.exe

- Make will complain about “git not found” but will compile anyway.
- This takes about 10 minutes, 2 minutes in Win 10 with a SSD.

***The following message means you did not clone the latest release. Go back to the Install Particle Firmware step.

## FAQ

***This message means you installed wrong version of firmware from github

## Step 9: Install myWindCode

1. Using Windows Explorer copy myWindCode folder to GitHub\firmware\user\applications
Or GitHub\firmware-develop\user\applications
  - You could use Link Shell Extension to link the folder
right click on GitHub\Wind\myWindCode
pick link source
browse to GitHub\firmware\user\applications
drop as symbolic link
If needed, using your favorite editor, add the line:
#include <Particle.h>

after the line #include “application.h”
The application must have suffix “.cpp” e.g. myWindCode.cpp

## Redo Loop

make PLATFORM=photon APP=blink program-dfu

With photon in dfu mode go to main folder using cmd as administrator
cd ../../Users/210023782/Documents/GitHub/firmware/main
cd ../../Users/Dave/Documents/GitHub/firmware/main
cd ../../Users/Dave/Documents/GitHub/firmware-develop/main
make all PLATFORM=photon APP=myWindCode
make PLATFORM=photon APP=myWindCode program-dfu
dfu-util -d 2b04:d006 -a 0 -i 0 -s 0x80A0000:leave -D ../build/target/user-part/platform-6-m/myWindCode.bin
--or--
make all program-dfu PLATFORM=photon APP=myWindCode
make clean all program-dfu PLATFORM=photon APP=myWindCode

Super Clean Redo Loop
1. Get the newest firmware from origin/develop using GitHub
2. go into the modules folder, and run w/ the Photon in dfu mode
make clean all program-dfu PLATFORM=photon
The two system firmwares will be updated, and then the user firmware. Will complain about git.
4. Modify user\src\application.cpp for your code
5. Go into the main folder, and run stuff above
cd ..\main

## Visual Studio IDE

- With this method, the Visual Studio Code process that calls ‘particle’ will not work. The compiler never finds the main.cc file.
  - To make the old process work, need myWindCode.ino or myWindCode.cpp application file without the #include “main.h” line.

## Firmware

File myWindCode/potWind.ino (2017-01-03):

//Sometimes useful for debugging
//#pragma SPARK_NO_PREPROCESSOR
//

// Standard
#ifdef ARDUINO
#include <Servo.h>
#include <Arduino.h>     // Used instead of Print.h - breaks Serial
#else                    // Photon
#include "application.h" // Should not be needed if file ino or Arduino
SYSTEM_THREAD(ENABLED); // Make sure code always run regardless of network status
#endif
#include "myAnalyzer.h"
#include "myTables.h"
#include "math.h"

// Test features
#define VECTOR
//#define FREQUENCY
//#define STEPS
typedef enum {FREQ, STEP, VECT} testType;
#ifdef VECTOR
testType testOnButton = VECT;
#endif
#ifdef FREQUENCY
testType testOnButton = FREQ;
#endif
#ifdef STEPS
testType testOnButton = STEP;
#endif
extern int  verbose    = 1;     // [1] Debug, as much as you can tolerate.   For Photon set using "v#"
extern bool bareOrTest = false; // [false] Fake inputs and sensors for test purposes.  For Photon set using "t"
double stepVal         = 6;     // [6] Step input, %nf.  Try to make same as freqRespAdder

/*
Controlling a servo position using a potentiometer (variable resistor)
by Dave Gutz

Connections for Photon:
  ESC ------------------- Photon
    BLK ------------------- GND
    WHT ------------------- PWM Output (A4)
  ESC----------------- 3-wire DC Servomotor
    Any three to any three
  DPST switch-------------Photon
    GND-------------------D4
  DPST switch
    HI--------------------3.3V
    LO--------------------10K to GND
  Push button-------------Photon
      R---------------------D2
    Push button
      HI--------------------3.3V
      LO--------------------10K to GND
  F2V---------------------Photon
    V5/V10----------------Analog In A2
    GND-------------------GND
  POT---------------------Photon
    VHI ------------------3.3v
    VLO ------------------GND
    WIPE -----------------Analog In A0
  LED to indicate frequency response----Digital Output (D7)
  Hardware Platform:
    Microcontroller:  Particle Photon
    ESC:Turnigy Plush 25A, 2-4S LiPo
    Power Supply:  BINZET AC 100-240V to DC 12V 10A
    Potentiometer:  Mouser 314-1410F-10K-3  10K Linear Pot
    Motor:  Hobby King 50mm Alloy EDF 4800 Kv (3s Version)
    F2V:  Texas Instruments 926-LM2907N/NOPB (14 pin, no Zener)


Connections for Arduino:
  ESC ------------------- Arduino
    BLK ------------------- GND
    WHT ------------------- PWM Output (5)
  ESC----------------- 3-wire DC Servomotor
    Any three to any three
  F2V-----------------Arduino
    V5/V10----------------Analog In A2
    GND-------------------GND
  DPST switch-------------Arduino
    CTR-------------------4
  DPST switch
    HI--------------------3.3V
    LO--------------------10K to GND
  Push button-------------Arduino
    R---------------------2
  Push button
    HI--------------------3.3V
    LO--------------------10K to GND
  POT---------------------Arduino
    VHI ------------------5V
    VLO ------------------GND
    WIPE -----------------Analog In A0
  BUTTON ----------------Ardunio  D2
    see https://www.arduino.cc/en/Tutorial/Button
  LED to indicate frequency response----Digital Output (7)
  JUMPER---------------4 to GND for Closed Loop
  Hardware Platform:
    Microcontroller:  Arduino Uno R3
    ESC:Turnigy Plush 25A, 2-4S LiPo
    Power Supply:  BINZET AC 100-240V to DC 12V 10A
    Potentiometer:  Mouser 314-1410F-10K-3  10K Linear Pot
    Motor:  Hobby King 50mm Alloy EDF 4800 Kv (3s Version)
    F2V:  Texas Instruments 926-LM2907N/NOPB (14 pin, no Zener)

  Reaquirements:
  Prime:
  1.  Inputs:  fan speed, pushbutton, slide switch, potentiometer
  2.  Outputs: ESC command using TTL/PWM servo control library
  3.  Manually sweep ESC command from min to max using pot.
  4.  Limit ESC command for safety using configurable parameters.
  5.  Turn on to minimum ESC input level.  Calibration of the ESC is done elsewhere.
  6.  Switch from open to closed loop and vice versa with small, <5 deg throttle
      bump, in response to switch change.
  7.  Perform frequency response analysis in response to button push.
  8.  Update closed loop algorithms, sense inputs, and produce outputs at rate
      at least as fast as 0.015 second update rate.
  Secondary:
  1.  Repeated Pushbutton toggles frequency response in progress.   When
      restarting, it begins completely fresh.
  2.  For non-Arduino, may also use a software Pushbutton - send string on serial.
  3.  Embed a plant model for dry code checkouts.
  4.  Filter pot noise.

  Tasks TODO:
  1.  Photon frequency response with button

  Revision history:
    31-Aug-2016   DA Gutz   Created
    13-Sep-2016   DA Gutz   Initial analyzing
    30-Sep-2016   DA Gutz   Arduino added
    10-Oct-2016   DA Gutz   First frequency response completion
    30-Oct-2016   DA Gutz   Gain scheduling
    16-Nov-2016   DA Gutz   Retune again again

  Distributed as-is; no warranty is given.
*/

// Test features usually commented
//

// Disable flags if needed.  Usually commented
//#define DISTURB_CONTROL                       // Use disturbance rejection gains in CLAW
//#define USE_FIXED_LL                          // Use the fixed lead lag compensator

// Constants always defined
// #define CONSTANT
#ifdef ARDUINO
#define BUTTON_PIN 2                                           // Button 3-way input momentary 3.3V, steady GND (D2)
#define PWM_PIN 5                                              // PWM output (PD5)
#define POT_PIN A0                                             // Potentiometer input pin on Arduino (PC0)
#define F2V_PIN A2                                             // Fan speed back-emf input pin on Arduino (PC2)
#define CL_PIN 4                                               // Closed loop 3-way switch 5V or GND (D4 to GND)
#define CLOCK_TCK 16UL                                         // Clock tick resolution, micros
#define INSCALE 1023.0                                         // Input full range from OS
const double vpotHalfDB = 0.15;                                // Half deadband sliding deadband filter, volts
const double POT_MAX = 5.0;                                    // Maximum POT value, vdc
const double F2V_MAX = 5.0;                                    // Maximum F2V value, vdc
const double POT_BIA = 0.36 + vpotHalfDB;                      // Pot adder, vdc
const double POT_SCL = (4.6 - vpotHalfDB - POT_BIA) / POT_MAX; // Pot scalar, vdc
#else                                                          // Photon
#define BUTTON_PIN D2                                          // Button 3-way input momentary 3.3V, steady GND (D2)
#define PWM_PIN A4                                             // PWM output (A4)
#define POT_PIN A0                                             // Potentiometer input pin on Photon (A0)
#define F2V_PIN A2                                             // Fan speed back-emf input pin on Photon (A2)
#define CL_PIN D0                                              // Closed loop 3-way switch 3.3V or GND  (D0)
#define CLOCK_TCK 8UL                                          // Clock tick resolution, micros
#define INSCALE 4096.0                                         // Input full range from OS
const double vpotHalfDB = 0.0;                    // Half deadband sliding deadband filter, volts
const double POT_MAX = 3.3;                       // Maximum POT value, vdc
const double F2V_MAX = 3.45;                      // Maximum F2V value, vdc
const double POT_BIA = 0.0;                       // Pot adder, vdc
const double POT_SCL = (3.3 - POT_BIA) / POT_MAX; // Pot scalar, vdc
#endif
//********constants for all*******************
#define PUBLISH_DELAY 15000UL // Time between cloud updates (), micros
#define CONTROL_DELAY 15000UL // Control law wait (), micros
#define FR_DELAY 4000000UL    // Time to start FR, micros
const double F2V_MIN = 0.0;   // Minimum F2V value, vdc
const double POT_MIN = 0;     // Minimum POT value, vdc
const double DENS_SI = 1.225; // Air density, kg/m^3

// Test
bool freqResp = false;             // Perform frequency response test status
bool vectoring = false;            // Perform vector test status
const int nsigFn = 4;              // Length of fn
const int ntfFn = 2;               // Number of transfer  functions to calculate <= length(ix)
double fn[4] = {0, 0, 0, 0};       // Functions to analyze
const int ix[2] = {0, 0};          // Indeces of fn to excitations
const int iy[2] = {1, 2};          // Indeces of fn to responses
const double freqRespScalar = 1e8; // Use 40 for +/-3 deg, 20 for +/-6 deg, 13 for +/-10 at 50% Nf
const double freqRespAdder = 6;    // +/- deg

//
// Dependent includes
#include "myCLAW.h"
#include "myFilters.h"

// Global variables
double throttle = -5; // Servo value, 0-179 degrees
char buffer[256];
LagTustin *throttleFilter; // Tustin lag noise filter
FRAnalyzer *analyzer;      // Frequency response analyzer
Servo myservo;             // create servo object to control dc motor
ControlLaw *CLAW;          // Control Law

#ifndef ARDUINO
String inputString = "";        // a string to hold incoming data
boolean stringComplete = false; // whether the string is complete
#endif

#ifdef VECTOR
// Test vector setup (functions at bottom of this file)
bool Vcomplete(void);
double Vcalculate(double);
void Vcomplete(bool);
const double Vtv_[] =  {0, 8,  10, 12, 14, 16, 18, 20, 22, 24, 26, 28, 30, 32, 34, 36, 38, 44}; // Time, s
const double Vvv_[] =  {6, 18, 30, 42, 54, 66, 78, 90, 96, 90, 78, 66, 54, 42, 30, 18, 6,  6};  // Excitation
const unsigned int Vnv_ = sizeof(Vtv_)/sizeof(double);  // Length of vector
double Voutput_ = 0;        // Excitation value
double Vtime_ = 0;          // Time into vector, s
double VtnowStart_ = 0;     // now time of vector start reference, s
bool Vcomplete_ = false;    // Status of vector, T=underway
unsigned int Viv_ = 0;      // Index of present time in vector
#endif

void setup()
{
#ifndef ARDUINO
  WiFi.disconnect();
#endif
  pinMode(BUTTON_PIN, INPUT);
  Serial.begin(230400);
  myservo.attach(PWM_PIN, 1000, 2000); // attaches the servo.  Only supported on pins that have PWM
  pinMode(POT_PIN, INPUT);
  pinMode(F2V_PIN, INPUT);
  pinMode(CL_PIN, INPUT);

  // Lag filter
  double T = float(CONTROL_DELAY) / 1000000.0;
  throttleFilter = new LagTustin(T, tau, -0.1, 0.1);

#ifdef FREQUENCY
  // Frequency Response
  //                        wmin    wmax  dw    minCy numCySc  iniCy  wSlow
  analyzer = new FRAnalyzer(-0.8,   1.4,  0.1,  2,    1.0,     6,     1 / tauG,
                            double(CONTROL_DELAY / 1e6), ix, iy, nsigFn, ntfFn, "t,ref,exc,thr,mod,nf,T"); // 15 ms any
#endif

  myservo.write(throttle);

// Serial headers used by plotting programs
// Header for analyzer.  TODO:  should be done in analyzer.cpp so done when needed
#ifndef ARDUINO
  delay(5000); // Allow time to start serial monitor for Photon.  Ardino auto-starts
#endif
  /*
    analyzer->publish();
    Serial.println("");
    */
  // Header for time data
  if (verbose > 0)
  {
    //******************************************************************************************************************************
    sprintf(buffer, "time,mode,vpot,  pcntref,pcntSense,pcntSenseM,  err,state,thr, modPcng,T\n");
    Serial.print(buffer);
  }

#ifndef ARDUINO
  // Serial Event to allow switches to be passed in by user Serial transmit
  inputString.reserve(200); // Reserve 200 bytes for inputString Serial Event
#endif

  // Instatiate gain scheduling tables
  CLAW = new ControlLaw(T, DENS_SI);

#ifdef ARDUINO
  delay(100);
#else
  delay(1000);
  WiFi.off();
  delay(1000);
#endif
}
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

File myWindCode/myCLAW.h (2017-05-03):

#ifndef _myCLAW_h
#define _myCLAW_h

#include "myTables.h"
#include "myFilters.h"
#define CTYPE 1   // 0=P+I, 1=I, 2=PID
#define KIT   5    // -1=Photon, 0-5 = Arduino


#if   CTYPE==0  // P+I
#include "myPI.h"
#elif CTYPE==1  // I
#include "myI.h"
#elif CTYPE==2  // PID
#include "myPID.h"
#else
#error "Unknown CTYPE="
#endif


// Plant
static const double tau = 0.10;     // Input noise filter time constant, sec
static const double tldV = 0.0;     // Model F2V lead time constant, sec
static const double tauF2V = 0.1;   // Model F2V lag time constant, sec
static const double tldG = 0.0;     // Model Gas Generator lead time constant, sec
static const double tauG = 0.1;     // Model Gas Generator lag time constant, sec
static const double tldT = 0.0;     // Model Turbine lead time constant, sec
static const double NG_MIN = 0;     // Minimum trim, %Ng
static const double RATE_MAX = 240; // Maximum throttle change rate, deg/sec to avoid lockout
// See calibration<date>.xlsx for these hardware conversion derivations
static const double RPM_P = 461;                   // (rpm/%)
static const double THTL_MIN = 0;   // Minimum throttle, deg
static const double AREA_SI = 0.002121;            // Flow area, m^2
static const double NM_2_FTLBF = 0.738;            // ft-lbf/N-m conversion
static const double J = 3.743e-8;   // Turbine inertia, (rpm/s)/(ft-lbf)
static const double D_SI = 0.055;                  // Turbine dia, m
static const double FG_SI = 4.425;                 // Thrust at rated speed, N
static const double THTL_MAX = 180; // Maximum throttle, deg
static const double NG_MAX = 100;   // Maximum trim, %Ng

static const double P_LTALL_NG[2] = {-25454, 13062};  // Common coeff throttle(deg) to NG(rpm)
static const double P_NGALL_NT[2] = {-7208, 1.0000};  // Coeff NG(rpm) to NT(rpm)
static const double P_NTALL_NG[2] = {-7208, 1.0000};  // Coeff NG(rpm) to NT(rpm)
//
// Generic throttle-->Ng used in control laws.   These characteristics below (except xALL) are for test consistency.
// xALL nominally used to calibrate for a wildly different tauT on some kits.   Then problem can concentrate on gain variations.
#if KIT==-1
// CalPhotonTurnigy 12/24/2016
static const double xALL[6] = {0.,    16.,    25.,    47.5,   62.,    80.};   // Gain breakpoints, %Nt
static const double P_V4_NT[3] = {0, 28857, 296};  // Coeff V4(v) to NT(rpm)
//static const double P_LT_NG[2] = {-35968, 15569};  // Coeff throttle(deg) to NG(rpm)
static const double P_NG_NT[2] = {-4629, 0.9778};  // Coeff NG(rpm) to NT(rpm)
static const double P_NT_NG[2] = {4826,  1.0194};  // Coeff NT(rpm) to NG(rpm)
static const double DCPDL = -1.765;                // dCpdLambda, dimensionless.  Cp is power coefficient and Lambda is speed tip ratio
static const double LAMBDA = 3.17;                 // Turbine tip speed ratio to air velocity, dimensionless
static const double DELTAV = 5.0;                  // Air velocity turbine first moves, m/s
#elif KIT==0
// Ard1_Turn0_ESC0_G0b_T0a 1/4/2017
static const double xALL[6] = {0.,    0.01,  27.2,    47.4,   75.1,    80.};   // Gain breakpoints, %Nt
static const double P_V4_NT[3] = {0, 13952,   27};  // Coeff V4(v) to NT(rpm)
//static const double P_LT_NG[2] = {-19172, 11411}; // Coeff throttle(deg) to NG(rpm)
static const double P_NG_NT[2] = {-8053, 0.9475};  // Coeff NG(rpm) to NT(rpm)
static const double P_NT_NG[2] = {8510,  1.0550};  // Coeff NT(rpm) to NG(rpm)
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

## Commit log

2017-01-03 Initial put
    [calibration20161207.xlsx, fr_header.xlsx, microturbineManifest20160930.xlsx, tr_header.xlsx]
2017-02-13 retune for classroom
    [calibration20170213.xlsx, matlabTuning20170213.xlsx]
2017-05-04 totally portable no wifi needed for anything
    Can use either Arduino IDE or Particle firmware CLI
2017-10-19 order more parts and DUE
    [microturbineManifest20161031.xlsx]
2017-11-22 Speed sense circuit board
    [arduinoDUE_Wind.fzz, speedSenseStripboard.fzz]
2017-11-22 match to first piece of speed sensor hardware
    [speedSenseStripboard.fzz]
2017-11-24 stripboard circuits
    [arduinoDUE_Wind.fzz, mosfetter.fzz, speedSenseStripboard.fzz]
2017-12-04 Begin to cal the new speed circuits
    [F2V_Cal20171203.xlsx]
2017-12-17 f2v cal through sn 5
    [F2V_Cal20171203.xlsx]
